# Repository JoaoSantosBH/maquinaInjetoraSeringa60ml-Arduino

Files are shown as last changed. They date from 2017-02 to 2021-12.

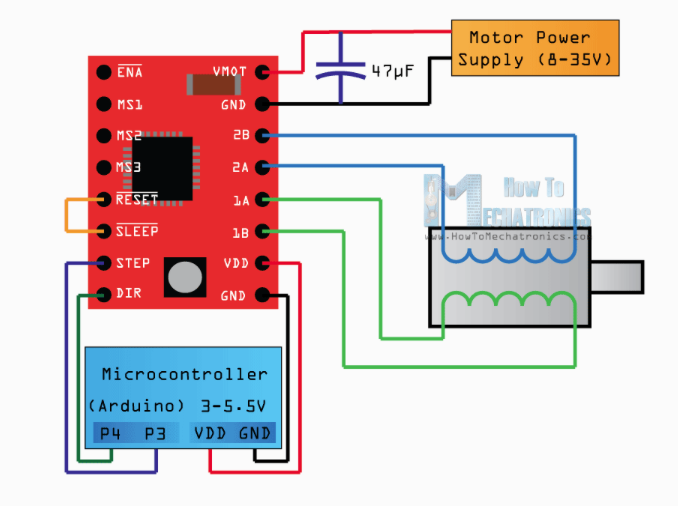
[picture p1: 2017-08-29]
docs/stepMotorA4988.png

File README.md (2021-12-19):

# Protótipo de Maquina Injetora para Seringa 60ml com Arduino


João Santos

Em 2015 devido a um estreitamento de esôfago (disfagia) causado por um câncer, minha mãe passou a se alimentar por uma sonda de [**Gastrostomia**](https://www.tuasaude.com/gastrostomia/) e a partir dai, passamos a conviver com problemas gerados pela alimentação através de sonda.

Durante dois anos observando esses problemas, me veio a motivação de construir um protótipo de uma máquina injetora para nutrição.

[Artigo](https://joaomarcelo-ms.medium.com/prot%C3%B3tipo-de-maquina-injetora-para-seringa-60ml-com-arduino-6b15f981d936)

Prototipo de maquina injetora de dieta liquida com seringa 60ML desenvolvido com Arduino;</br>

Projetada para infusão de dietas ricas em fibras e mais viscosas, em pacientes com restrição alimentar por via oral,</br>
 aumentando a qualidade alimentar do paciente, uma vez que permite alimentos mais viscosos e com isso mais ricos em fibras </br>
e nutrientes, ao contrário das dietas industrializadas que se dão por equipamentos (Equipo) que facilmente entopem,</br> impedindo o 
paciente de consumir dietas mais ricas em fibras e nutrientes;</br>

A duração da infusão é programada em 3 minutos para 60 ml de dieta, com intuito de evitar ulceração no paciente, devido ao </br>alimento 
entrar muito rapidamente, como é o caso, quando aplicado à mão, e aumentar a absorção do alimento pelo organismo.</br>

Neste caso a dieta pode ser ministrada lentamente, evitando o risco de ulcera e aumentando a absorção do alimento;</br>

Através de um App ou do botão na máquina o paciente ou seu cuidador, pode iniciar a injeção alimentar, e ao final da injeção</br>
 a maquina automaticamente retorna a posição inicial para aguardar nova carga de alimento, gerando maior conforto para o </br>paciente 
e/ou seu cuidador</br>

A máquina possui alertas visuais e sonoros para indicar seu status de funcionamento, e é portátil, podendo ser levada para onde for!</br>

Listagem dos componentes necessários:</br>
<ul>
<li>1 Arduino MEGA/UNO</li>
<li>1 buzzer</li>
<li>1 led vermelho</li>
<li>1 led verde</li>
<li>3 chaves tacteis</li>
<li>2 chaves fim de curso</li>
<li>5 resistores 100Ω</li>
<li>1 capacitor eletrolitico 100µF 16V</li>
<li>1 motor passo nema 14</li>
<li>1 drive A4988 (necessário regular a corrente para 0.7 A)</li>
<li>1 seringa 60ml</li>
<li>1 estrutura base maquina (projeto 3D para impressão em anexo)</li>
<li>1 Acoplamento Flexivel/cnc/motor Passo 5x5 Mm</li>
<li>1 barra parafuso 5mm - 1m </li>
<li>2 porcas sextavadas 5mm</li>
<li>1 protoboard</li>
<li>1 fonte 12V 1A</li>
<li>1 chapa mdf 300mm x 50mm x 6mm</li>
<li>1 rolamento 2.2cm ø</li>
<li>Kit Jumpers Macho-Macho</li>
</ul>

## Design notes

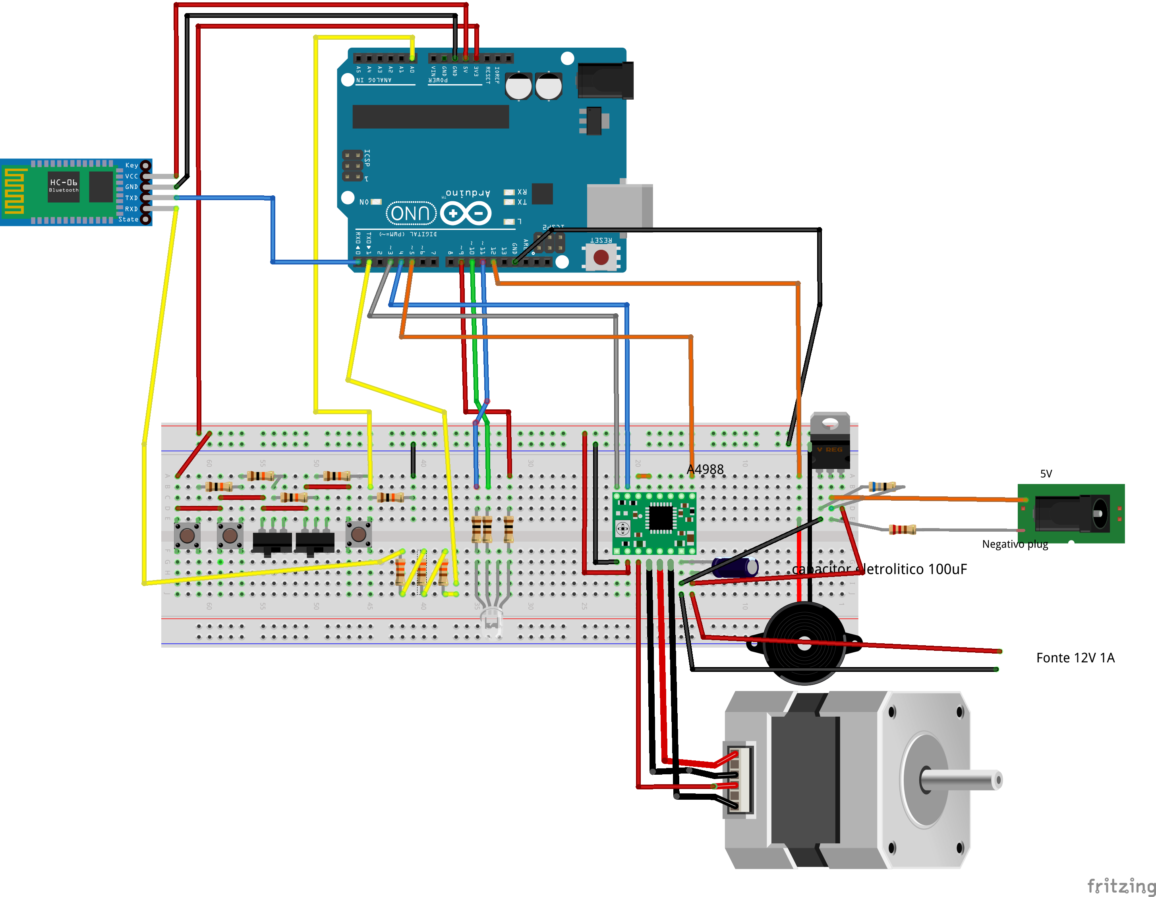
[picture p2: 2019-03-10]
docs/PROTOBOARD_uno.png

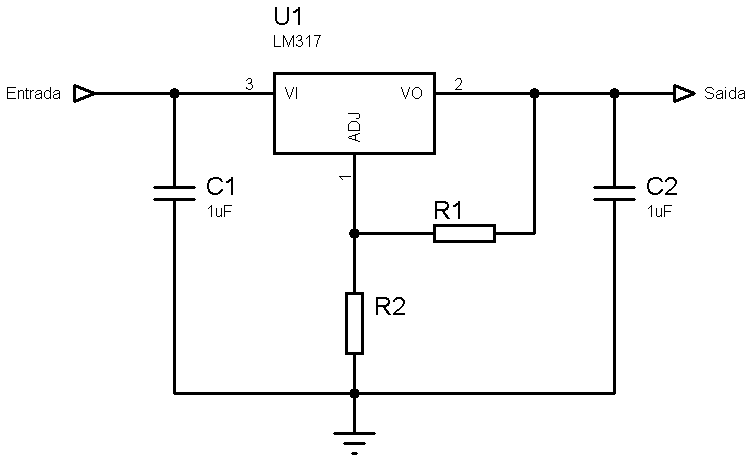
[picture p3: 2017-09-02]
docs/CILM317.png

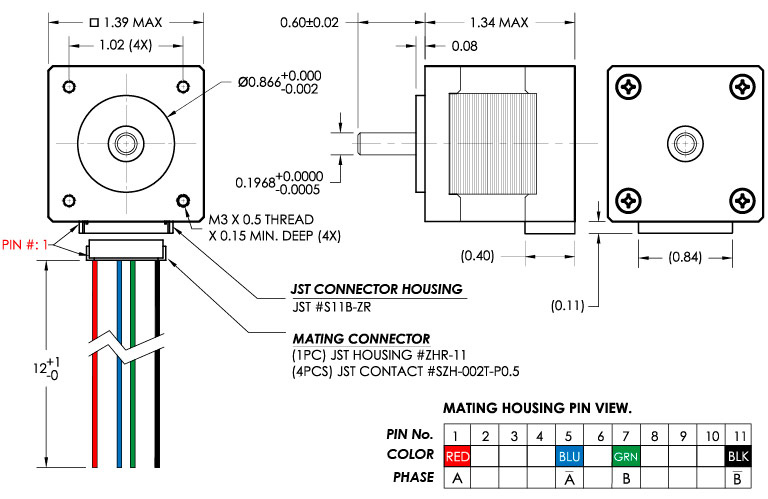
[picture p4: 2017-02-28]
docs/nema14eletric.jpg

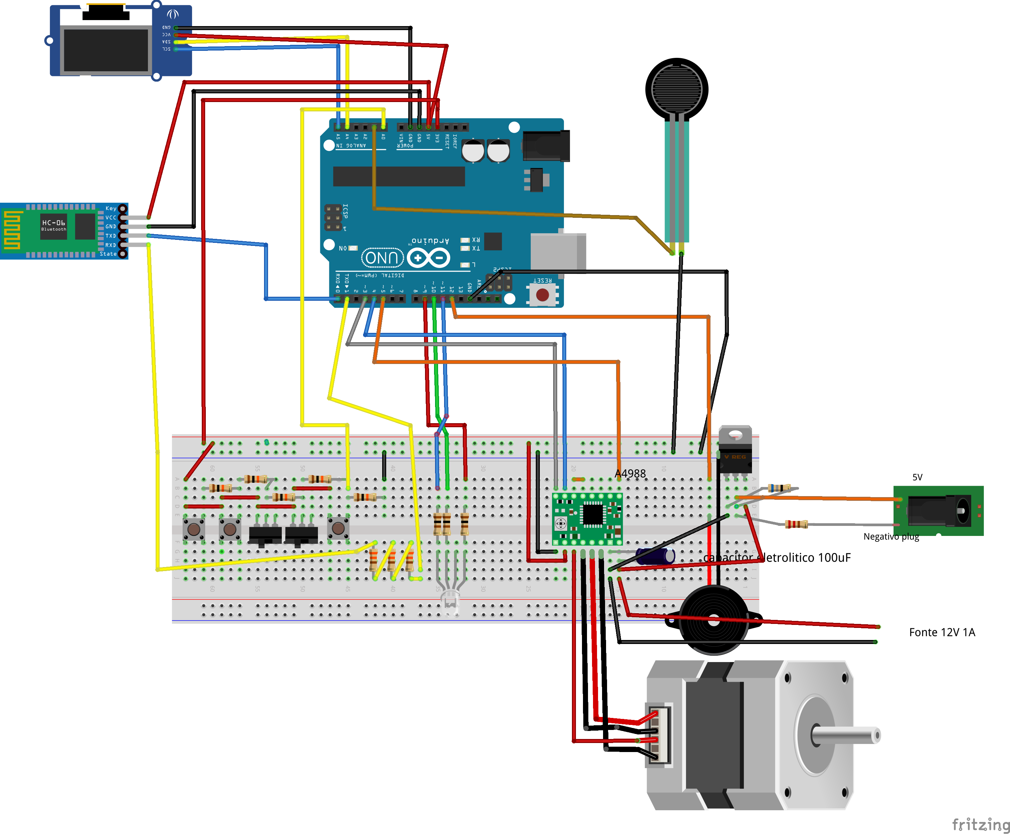
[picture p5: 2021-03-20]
fritzing/pcb_bb.png

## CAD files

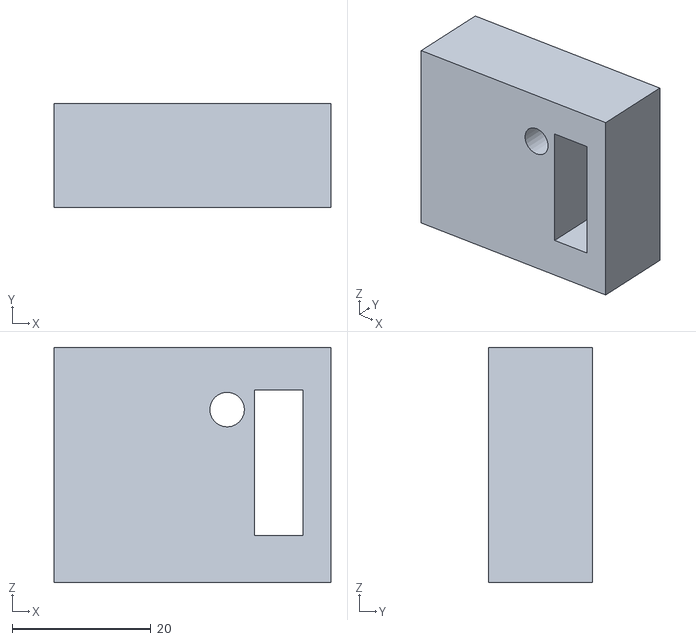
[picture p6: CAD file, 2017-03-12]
stl/FimCurso.stl
40.0 x 15.0 x 34.0

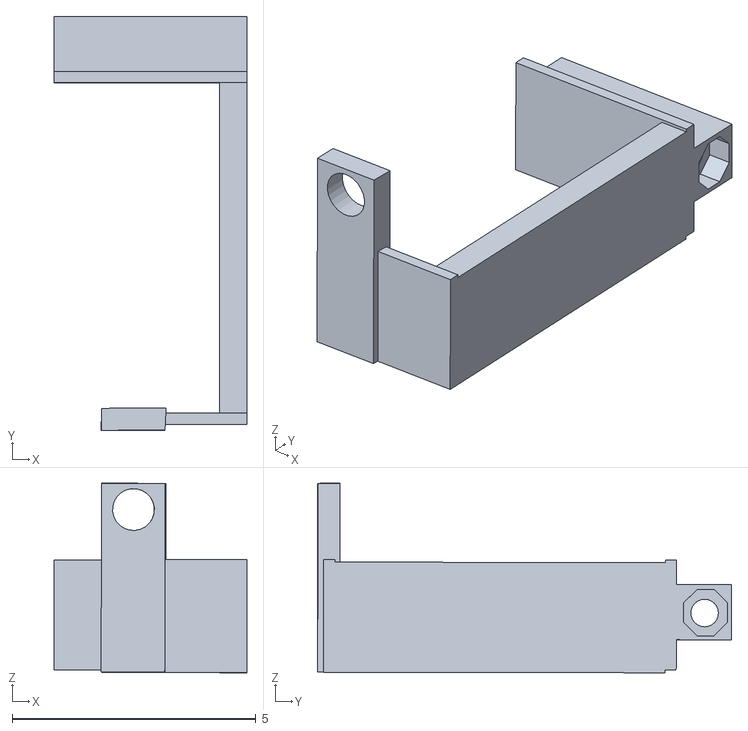
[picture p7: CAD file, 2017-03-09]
stl/suporteEmboloSeringaScale.stl
3.96 x 8.49 x 3.89

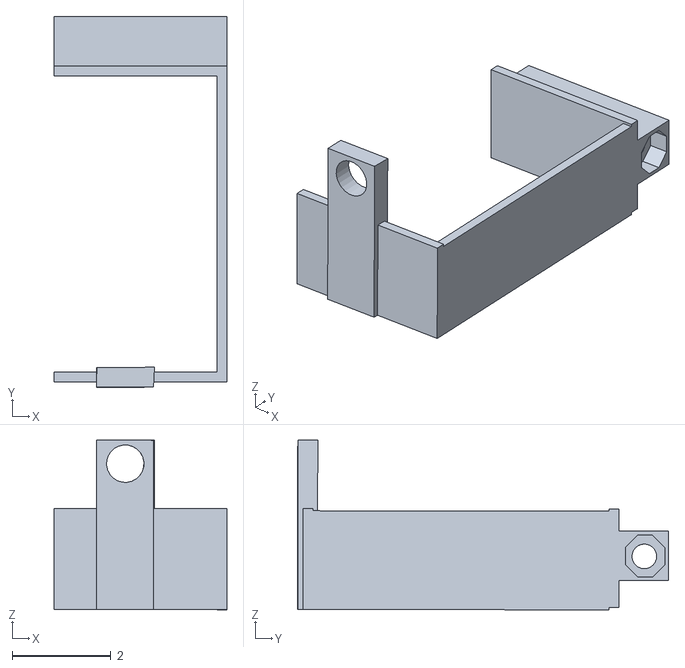
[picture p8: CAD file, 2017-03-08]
stl/SuporteEmbolo.stl
3.50 x 7.52 x 3.44

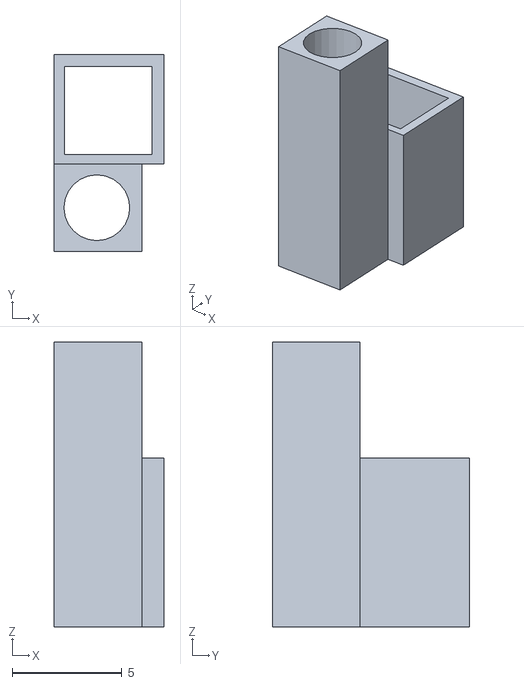
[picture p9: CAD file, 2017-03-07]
stl/estrutura.stl
5.00 x 9.00 x 13.0

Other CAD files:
old_stuff/sketchup/FimCurso.skp
old_stuff/sketchup/baeseMadeira.skp
old_stuff/sketchup/estrutura_modelo3D.skp
old_stuff/sketchup/suporteEmboloSeringa.skp
old_stuff/sketchup/suporteEmboloSeringaScale.skp
sketchup/FimCurso.skp
sketchup/baeseMadeira.skp
sketchup/estrutura_modelo3D.skp
sketchup/suporteEmboloSeringa.skp
sketchup/suporteEmboloSeringaScale.skp

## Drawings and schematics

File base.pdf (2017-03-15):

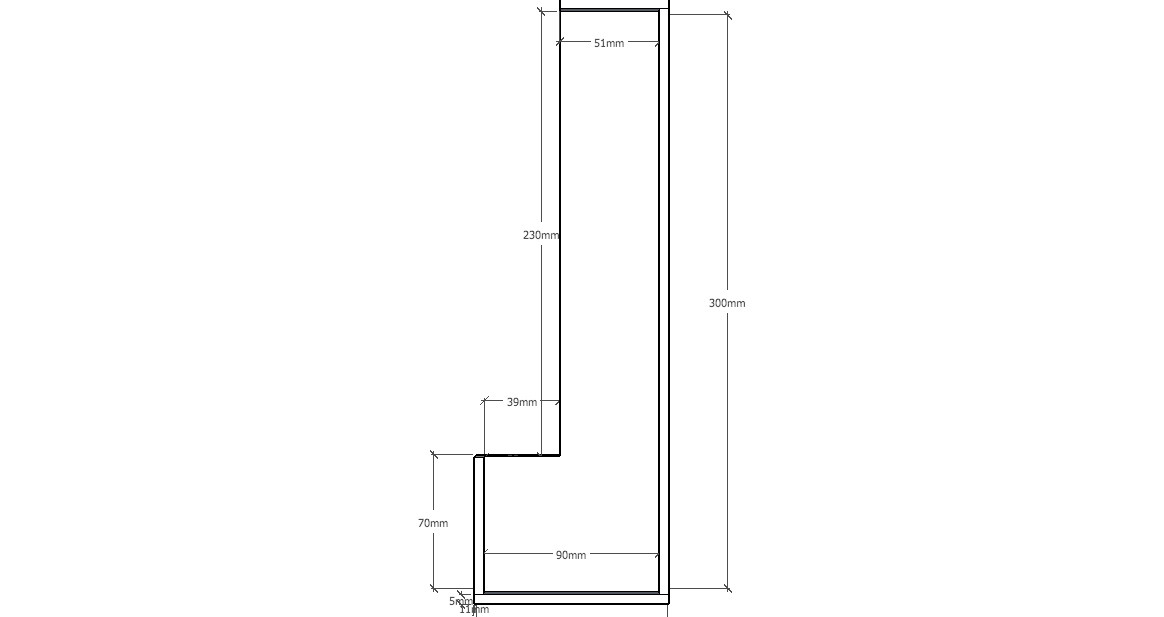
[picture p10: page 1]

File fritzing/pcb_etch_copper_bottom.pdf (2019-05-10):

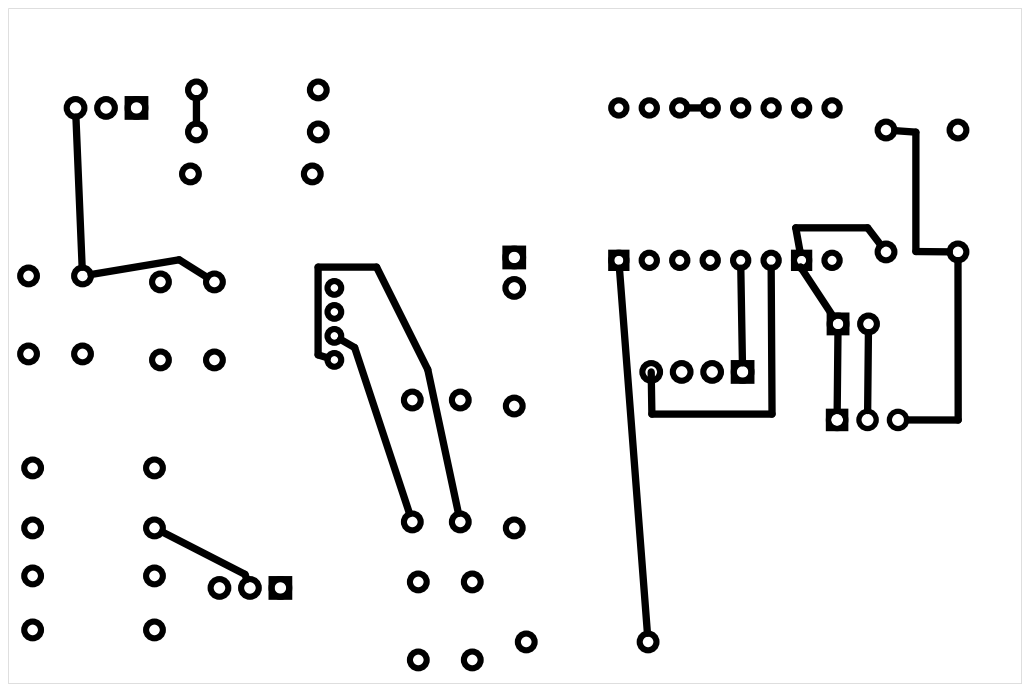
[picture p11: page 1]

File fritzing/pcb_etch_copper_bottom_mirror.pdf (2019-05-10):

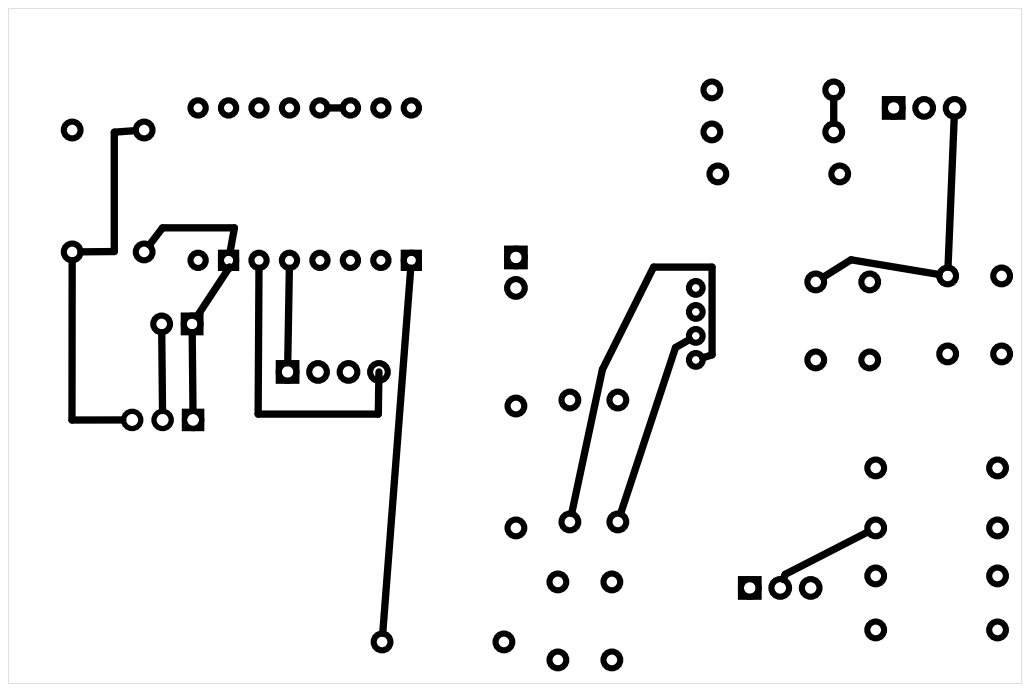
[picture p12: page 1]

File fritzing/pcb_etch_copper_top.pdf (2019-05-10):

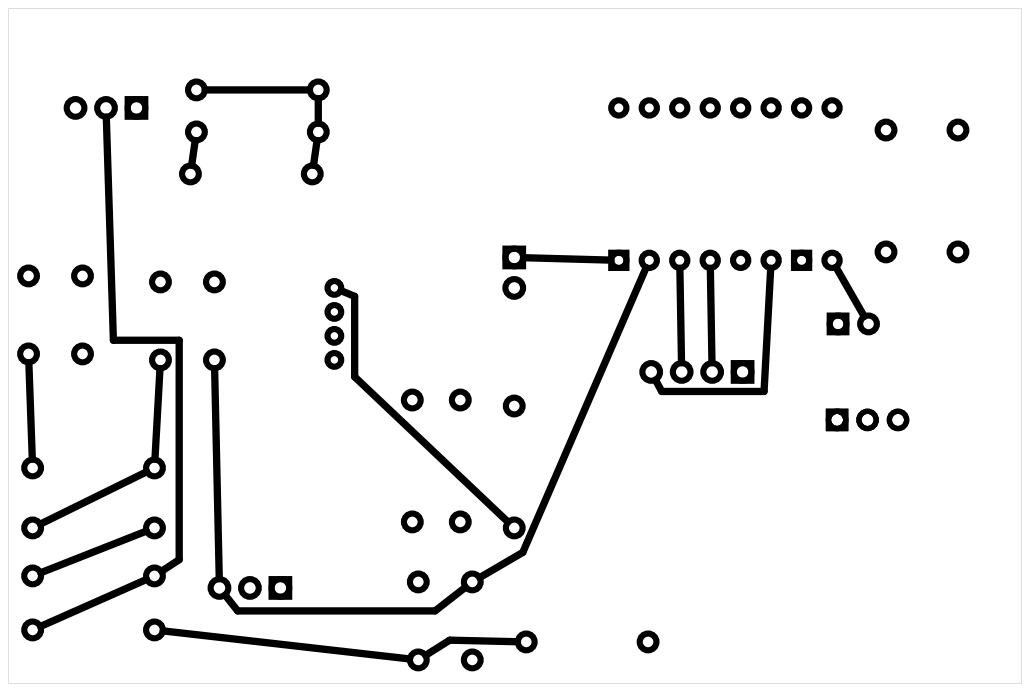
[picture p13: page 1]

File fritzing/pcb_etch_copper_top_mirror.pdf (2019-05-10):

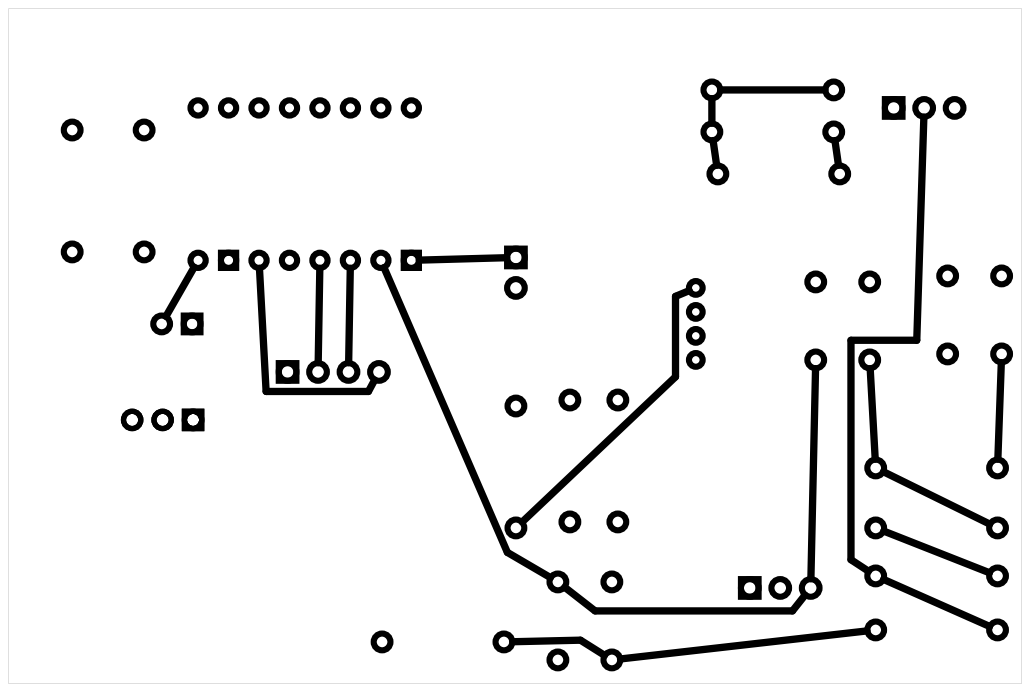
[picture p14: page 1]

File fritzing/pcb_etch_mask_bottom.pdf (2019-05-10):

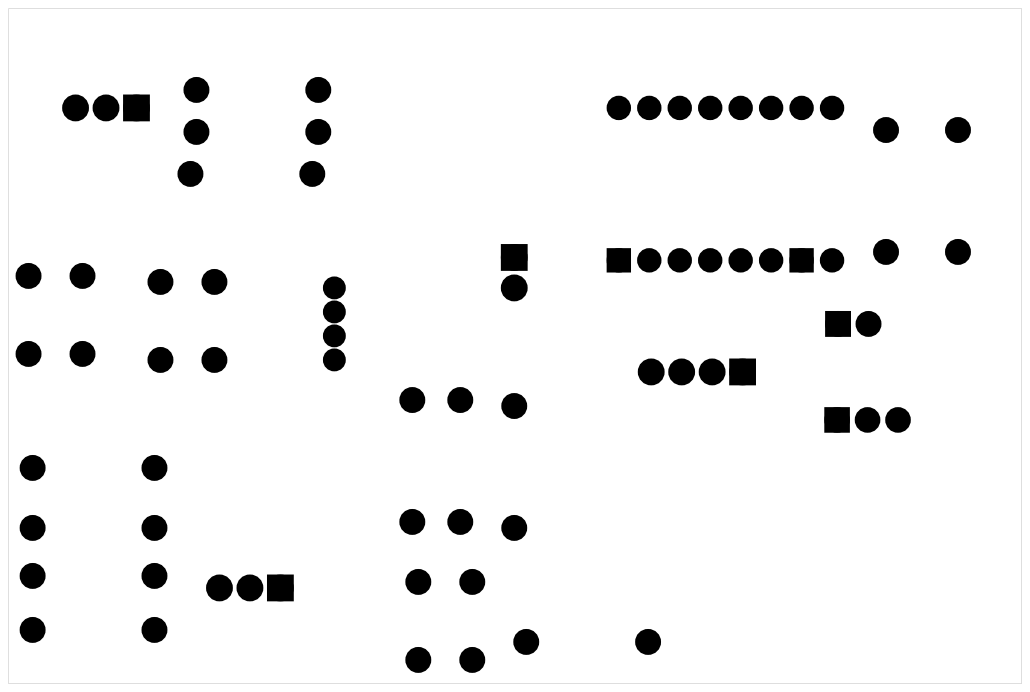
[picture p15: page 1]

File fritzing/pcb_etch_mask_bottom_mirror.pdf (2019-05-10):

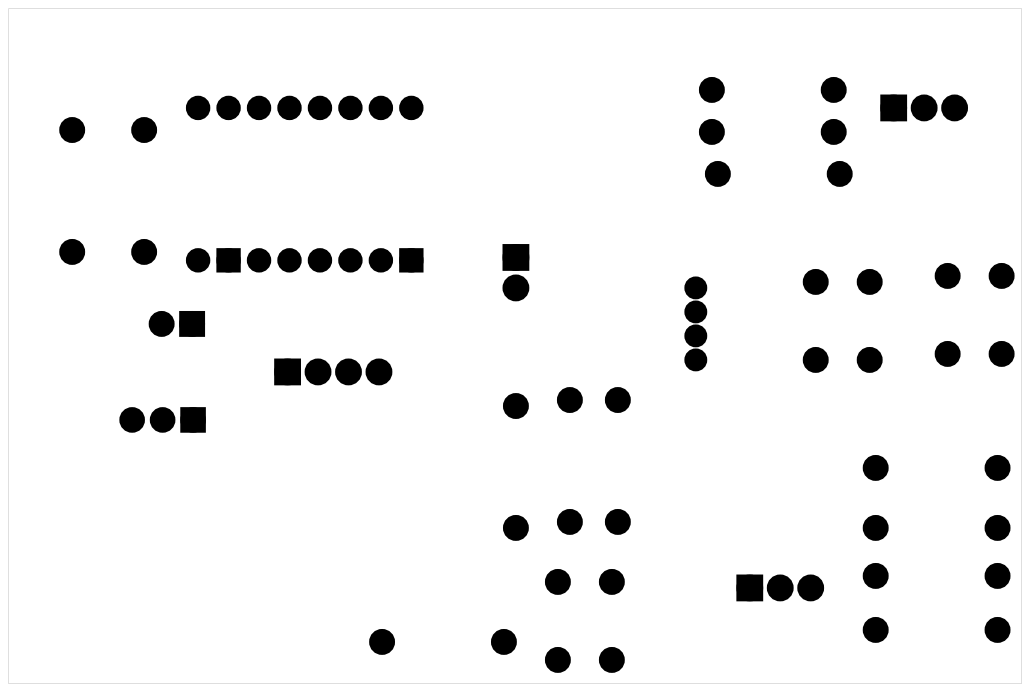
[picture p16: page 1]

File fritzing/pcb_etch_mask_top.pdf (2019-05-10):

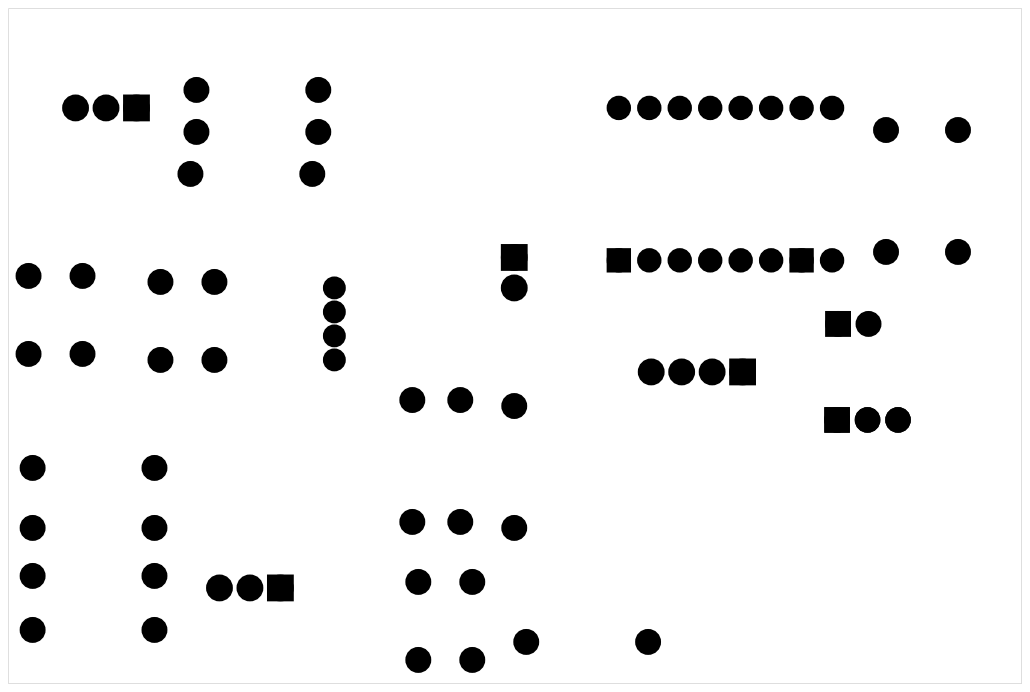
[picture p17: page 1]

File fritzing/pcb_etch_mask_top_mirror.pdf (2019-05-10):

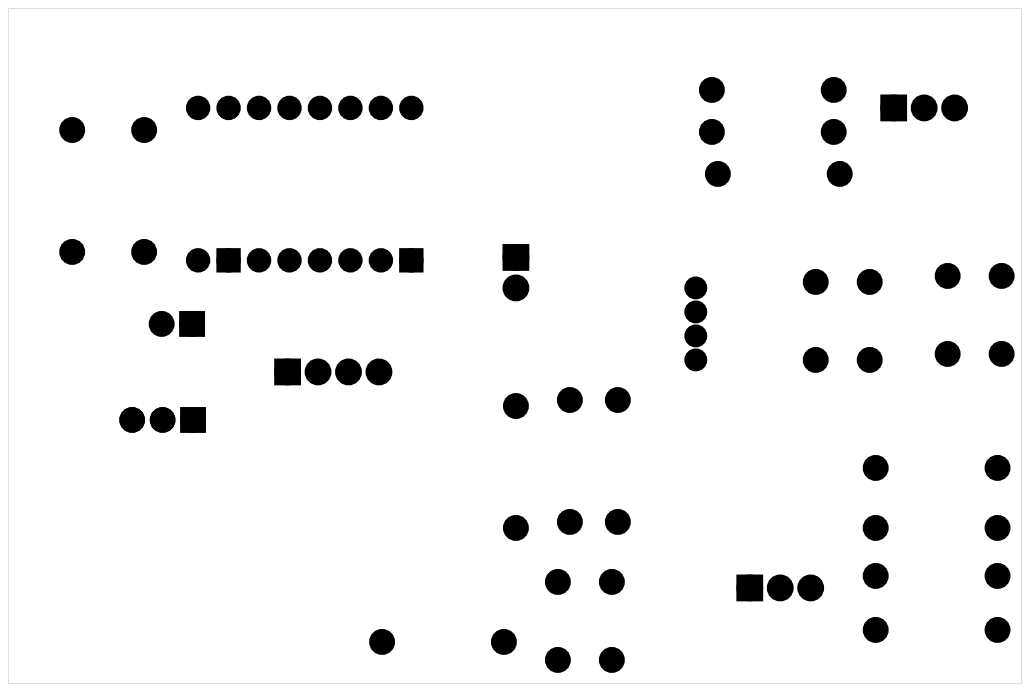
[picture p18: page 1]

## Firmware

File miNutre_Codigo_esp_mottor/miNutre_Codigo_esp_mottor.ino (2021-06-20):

//  MAQUINA INJETORA DE DIETA VIA SERINGA 60ML

// 10-03-2019
// VERSAO 1.1.0
//mar 2021

#include <AccelStepper.h>
#include <U8g2lib.h>
U8G2_SSD1306_128X64_NONAME_F_HW_I2C u8g2(U8G2_R0, /* reset=*/ U8X8_PIN_NONE, /* clock=*/ 5, /* data=*/ 4);   // ESP32 Thing, HW I2C with pin remapping

const uint8_t logo[] PROGMEM = {
  0x00, 0x00, 0x00, 0x00, 0x00, 0x00, 0x00, 0x00, 0x00, 0x00, 0x00, 0x00, 0x00, 0x00, 0x00, 0x00,
  0x00, 0x00, 0x00, 0x00, 0x00, 0x00, 0x00, 0x00, 0x00, 0x00, 0x00, 0x00, 0x00, 0x00, 0x00, 0x00,
  0x00, 0x00, 0x00, 0x00, 0x00, 0x00, 0x00, 0x00, 0x00, 0x00, 0x00, 0x00, 0x00, 0x00, 0x00, 0x00,
  0x03, 0xff, 0xff, 0xff, 0xff, 0xff, 0xff, 0xff, 0xff, 0xff, 0xff, 0xff, 0xff, 0xff, 0xff, 0xc0,
  0x07, 0xff, 0xff, 0xff, 0xff, 0xff, 0xff, 0xff, 0xff, 0xff, 0xff, 0xff, 0xff, 0xff, 0xff, 0xe0,
  0x07, 0xff, 0xff, 0xff, 0xff, 0xff, 0xff, 0xff, 0xff, 0xff, 0xff, 0xff, 0xff, 0xff, 0xff, 0xe0,
  0x07, 0x00, 0x00, 0x00, 0x00, 0x00, 0x00, 0x00, 0x00, 0x00, 0x00, 0x00, 0x00, 0x00, 0x00, 0x60,
  0x07, 0x00, 0x00, 0x00, 0x00, 0x00, 0x00, 0x00, 0x00, 0x00, 0x00, 0x00, 0x00, 0x00, 0x00, 0x60,
  0x07, 0x00, 0x00, 0x00, 0x00, 0x00, 0x00, 0x00, 0x00, 0x00, 0x00, 0x00, 0x00, 0x00, 0x00, 0x60,
  0x07, 0x00, 0x00, 0x00, 0x00, 0x00, 0x00, 0x00, 0x00, 0x00, 0x00, 0x00, 0x00, 0x00, 0x00, 0x60,
  0x07, 0x00, 0x00, 0x00, 0x00, 0x00, 0x00, 0x00, 0x00, 0x00, 0x00, 0x00, 0x00, 0x00, 0x00, 0x60,
  0x07, 0x00, 0x00, 0x00, 0x00, 0x00, 0x00, 0x00, 0x00, 0x00, 0x00, 0x00, 0x00, 0x00, 0x00, 0x60,
  0x07, 0x00, 0x00, 0x00, 0x00, 0x00, 0x01, 0xfc, 0x00, 0x00, 0x3c, 0x00, 0x00, 0x00, 0x00, 0x60,
  0x07, 0x00, 0x00, 0x00, 0x00, 0x00, 0x1f, 0xfc, 0x00, 0x01, 0xfe, 0x00, 0x00, 0x00, 0x00, 0x60,
  0x07, 0x00, 0x00, 0x00, 0x00, 0x01, 0xff, 0xff, 0xc0, 0x1f, 0xfc, 0x00, 0x00, 0x00, 0x00, 0x60,
  0x07, 0x00, 0x00, 0x00, 0x00, 0x0f, 0xff, 0xff, 0xe0, 0xff, 0xf8, 0x00, 0x00, 0x00, 0x00, 0x60,
  0x07, 0x00, 0x00, 0x00, 0x00, 0xff, 0xff, 0xff, 0xef, 0xff, 0xc0, 0x00, 0x00, 0x00, 0x00, 0x60,
  0x07, 0x00, 0x00, 0xe0, 0x07, 0xff, 0xff, 0xff, 0xff, 0xfc, 0x00, 0x00, 0x00, 0x00, 0x00, 0x60,
  0x07, 0x00, 0x01, 0xf0, 0x3f, 0xff, 0xff, 0xff, 0xff, 0xe0, 0x00, 0x00, 0x1f, 0x00, 0x00, 0x60,
  0x07, 0x00, 0x01, 0xf3, 0xff, 0xff, 0xff, 0xff, 0xfe, 0x00, 0x00, 0x00, 0x60, 0x80, 0x00, 0x60,
  0x07, 0x00, 0x01, 0xff, 0xff, 0xff, 0xff, 0xff, 0xf0, 0x00, 0x00, 0x00, 0xc0, 0x40, 0x00, 0x60,
  0x07, 0x00, 0x01, 0xff, 0xff, 0xff, 0xff, 0xff, 0xf0, 0x00, 0x00, 0x00, 0x9e, 0x20, 0x00, 0x60,
  0x07, 0x00, 0x00, 0xff, 0xff, 0xff, 0xff, 0xff, 0xf0, 0x00, 0x00, 0x01, 0x11, 0x10, 0x00, 0x60,
  0x07, 0x00, 0x00, 0xff, 0xff, 0xff, 0xff, 0xff, 0xf0, 0x00, 0x00, 0x01, 0x11, 0x10, 0x00, 0x60,
  0x07, 0x08, 0x00, 0xff, 0xff, 0xff, 0xff, 0xff, 0xc0, 0x00, 0x00, 0x01, 0x1e, 0x10, 0x00, 0x60,
  0x07, 0x1e, 0x03, 0xff, 0xff, 0xff, 0xff, 0xff, 0xc0, 0x00, 0x00, 0x01, 0x12, 0x10, 0x00, 0x60,
  0x07, 0x3e, 0x3f, 0xff, 0xff, 0xff, 0xff, 0xff, 0xc0, 0x00, 0x00, 0x01, 0x13, 0x10, 0x00, 0x60,
  0x07, 0x3f, 0xff, 0xff, 0xff, 0xff, 0xff, 0xff, 0x80, 0x00, 0x00, 0x00, 0x91, 0x20, 0x00, 0x60,
  0x07, 0x3f, 0xff, 0xff, 0xff, 0xff, 0xff, 0xff, 0x00, 0x00, 0x00, 0x00, 0xc0, 0x60, 0x00, 0x60,
  0x07, 0x1f, 0xff, 0xff, 0xff, 0xff, 0xff, 0xfc, 0x00, 0x00, 0x00, 0x00, 0x60, 0x80, 0x00, 0x60,
  0x07, 0x1f, 0xff, 0xff, 0xff, 0xff, 0xff, 0xc0, 0x00, 0x00, 0x00, 0x00, 0x1f, 0x00, 0x00, 0x60,
  0x07, 0x1f, 0xff, 0xff, 0xff, 0xff, 0xfe, 0x00, 0x00, 0xc0, 0x00, 0x00, 0x00, 0x00, 0x00, 0x60,
  0x07, 0x1f, 0xff, 0xff, 0xff, 0xff, 0xe0, 0x00, 0x03, 0xc0, 0x00, 0x00, 0x00, 0x00, 0x00, 0x60,
  0x07, 0x1f, 0xff, 0xff, 0xff, 0xff, 0x00, 0x00, 0x0f, 0xc0, 0x00, 0x00, 0x00, 0x00, 0x00, 0x60,
  0x07, 0x0f, 0xff, 0xff, 0xff, 0xf0, 0x00, 0x00, 0x3f, 0xc0, 0x00, 0x00, 0x00, 0x00, 0x00, 0x60,
  0x07, 0x0f, 0xff, 0xdf, 0xff, 0x00, 0x00, 0x00, 0x7f, 0xc0, 0x00, 0x00, 0x00, 0x00, 0x00, 0x60,
  0x07, 0x0f, 0xfe, 0x1f, 0xf0, 0x00, 0x00, 0x00, 0x7f, 0xc0, 0x00, 0x00, 0x00, 0x00, 0x00, 0x60,
  0x07, 0x07, 0xe0, 0x0f, 0xc0, 0x00, 0x00, 0x00, 0xff, 0xc0, 0x00, 0x00, 0x00, 0x00, 0x00, 0x60,
  0x07, 0x07, 0xe0, 0x0f, 0xc0, 0x00, 0x00, 0x00, 0xff, 0xc0, 0x00, 0x00, 0x00, 0x00, 0x00, 0x60,
  0x07, 0x07, 0xe0, 0x0f, 0xc0, 0x00, 0x00, 0x00, 0xff, 0xc0, 0x00, 0x00, 0x00, 0x00, 0x00, 0x60,
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
};

#define STEP_PIN                   0
#define DIRECTION_PIN              2
#define MOTOR_ENABLE_PIN          15
#define PRESSURE_SENSOR           A0
#define BUTTONS                   A0
#define BUZZER                     16
#define BLUE                      13
#define GREEN                     12
#define RED                       14


AccelStepper myStepMotor(AccelStepper::DRIVER, STEP_PIN, DIRECTION_PIN );

char command;
String stringBluetooth;

String MACHINE_NAME = "m i N U T R E";
String RECALL = "RECALLn";
String WAIT   = "WAITING";
String INJECT = "INJECTn";
String START = "STARTIn";
String LOGO = "miNUTRE";

long myStepRevolutions = -1000000;

int preto     [3]  = { 0, 0, 0 };
int dimbranco [3]  = { 30, 30, 30};
int redValue = preto[0];
int greenValue = preto[1];
int blueValue = preto[2];
// VARIAVEIS DE CORES
int nRed = redValue;
int nGreen = greenValue;
int nBlue = blueValue;

int buttonBusStatus = 0;
int isInjecting  = 0;
int isWaiting = 1;
int isRecalling = 0;
int  botI = 1;
int  botR = 0;
int  botP = 0;
int  fcI  = 0;
int  fcR  = 0;
int pressureReading;
int incomingByte = 0;
int PULSE_WIDTH = 3;

int BT01_MIN = 200;
int BT01_MAX = 228;
int BT02_MIN = 240;
int BT02_MAX = 297;
int FDC01_MIN = 500;
int FDC01_MAX = 550;
int FDC02_MIN = 1000;
int FDC02_MAX = 1030;

void setup() {
  Serial.begin(115200);
  setupInOut();
  putMachineInReadyState();
  setupOled();
  printStatusOnSerial();
  drawInit();
  turnOnGreenLight();
  drawLogo();

}

void loop() {

  bluetoothCommandsListener();
  readComponentStatus();
  checkPressedButtons();
  checkBluetoothCommands();
  readInjectionPressure() ;
  //M O C K

  if (Serial.available() > 0) {
    // read the incoming byte:
    incomingByte = Serial.read();

    // say what you got:
    Serial.print("I received: ");
    Serial.println(incomingByte);

    if (incomingByte == 49) {
      startInjection() ;
    } else  if (incomingByte == 50) {
      stopInjectionAndPickup() ;
    } else  if (incomingByte == 48) {
      stopMachine() ;
    }
  }
  //M O C K
  myStepMotor.run();
}


void startInjection() {
  Serial.println("startInjection");
  settingInjectionStatus();
  turnOnBlueLight();
  drawInjet();
  settingInjectionMotor();
  stringBluetooth = "";
  printStatusOnSerial();
}

void stopInjectionAndPickup() {
  Serial.println("stopInjectionAndPickup");
  turnOnVioletLight();
  drawWait();
  settingStopRecallStatus();
  settingWaitMotor();
  printStatusOnSerial();
  pickupRecall();
}

void pickupRecall() {
  Serial.println("pickupRecall");
  settingRecallStatus();
  turnOnWhiteLight();
  drawRecall();
  settingRecallMotor();
  printStatusOnSerial();
}

void stopMachine() {
  Serial.println(" stopMachine");
  turnOnRedLight();
  drawWait();
  settingWaitStatus();
  settingWaitMotor();
  printStatusOnSerial();
  playHappyMelody();
}

void pressurePanic() {
  Serial.println(" pressurePanic");
  Serial.println("a pressão atingiu niveis alarmantes");
  turnOnRedLight();
  drawLogo();
  settingWaitStatus();
  settingWaitMotor();
  playImperialMarch();
  printStatusOnSerial();
}

void backALitle() {
  Serial.println("backALitle");
  turnOnGreenLight();
  drawLogo();
  settingWaitStatus();
  settingBackLittleMotor();
  delay(1000);
  drawWait();
  printStatusOnSerial();

}

void colorCrossFade(int cor[3]) {
  int R = (cor[0] * 255) / 100;
  int G = (cor[1] * 255) / 100;
  int B = (cor[2] * 255) / 100;
  int sweepRed = calcColorSweep(nRed, R);
  int sweepGreen = calcColorSweep(nGreen, G);
  int sweepBlue = calcColorSweep(nBlue, B);

  for (int i = 0; i <= 1020; i++) {
    redValue = calculateValue(sweepRed, redValue, i);
    greenValue = calculateValue(sweepGreen, greenValue, i);
    blueValue = calculateValue(sweepBlue, blueValue, i);
    analogWrite(RED, redValue);   // Write current valorues to LED pins
    analogWrite(GREEN, greenValue);
    analogWrite(BLUE, blueValue);
    delay(10);
  }
  nRed = redValue;
  nGreen = greenValue;
  nBlue = blueValue;
  delay(0);
}

int calcColorSweep(int previousValue, int finalValue) {
  int sweep = finalValue - previousValue;
  if (sweep) {
    sweep = 1020 / sweep;
  }
  return sweep;
}

int calculateValue(int sweep, int valor, int i) {
  if ((sweep) && i % sweep == 0) {
    if (sweep > 0) {
      valor += 1;
    }
    else if (sweep < 0) {
      valor -= 1;
    }
  }

  if (valor > 255) {
    valor = 255;
  }
  else if (valor < 0) {
    valor = 0;
  }
  return valor;
}

void turnOnGreenLight() {
  digitalWrite(GREEN, 255);
  digitalWrite(RED, 0);
  digitalWrite(BLUE, 0);
}
void turnOnRedLight() {
  digitalWrite(GREEN, 0);
  digitalWrite(RED, 255);
  digitalWrite(BLUE, 0);
}
void turnOnBlueLight() {
  digitalWrite(GREEN, 0);
  digitalWrite(RED, 0);
  digitalWrite(BLUE, 255);
}

void turnOnVioletLight() {
  digitalWrite(GREEN, 0);
  digitalWrite(RED, 255);
  digitalWrite(BLUE, 255);
}

void turnOnWhiteLight() {
  digitalWrite(GREEN, 255);
  digitalWrite(RED, 255);
  digitalWrite(BLUE, 255);
}

// THE IMPERIAL MARCH - John Williams
void playImperialMarch() {
  tone(BUZZER, 1500);
  delay(500);
  noTone(BUZZER);
  delay(50);
  tone(BUZZER, 1500);
  delay(500);
  noTone(BUZZER);
  delay(50);
  tone(BUZZER, 1500);
  delay(500);
  noTone(BUZZER);
  delay(50);
  tone(BUZZER, 1200);
  delay(250);
  tone(BUZZER, 1850);
  delay(250);
  noTone(BUZZER);
  delay(50);
  tone(BUZZER, 1500);
  delay(500);
  noTone(BUZZER);
  delay(50);
  tone(BUZZER, 1200);
  delay(250);
  tone(BUZZER, 1850);
  delay(250);
  tone(BUZZER, 1500);
  delay(500);
  noTone(BUZZER);
  delay(500);
  ///////////////////
  tone(BUZZER, 2220);
  delay(500);
  noTone(BUZZER);
  delay(50);
  tone(BUZZER, 2220);
  delay(500);
  noTone(BUZZER);
  delay(50);
  tone(BUZZER, 2220);
  delay(500);
  tone(BUZZER, 2369);
  delay(250);
  tone(BUZZER, 1850);
  delay(250);
  noTone(BUZZER);
  delay(50);
  tone(BUZZER, 1500);
  delay(500);
  noTone(BUZZER);
  delay(50);
  tone(BUZZER, 1200);
  delay(250);
  tone(BUZZER, 1850);
  delay(250);
  tone(BUZZER, 1500);
  delay(500);
  noTone(BUZZER);
}

void playHappyMelody() {
  tone(BUZZER, 1046);
  delay(125);
  noTone(BUZZER);
  delay(50);
  tone(BUZZER, 1318);
  delay(125);
  noTone(BUZZER);
  delay(50);
  tone(BUZZER, 1567);
  delay(125);
  noTone(BUZZER);
  delay(50);
  tone(BUZZER, 2093);
  delay(125);
  noTone(BUZZER);
  delay(50);
  tone(BUZZER, 2637);
  delay(125);
  noTone(BUZZER);
  delay(50);
  tone(BUZZER, 1046);
  delay(125);
  noTone(BUZZER);
  delay(50);
  tone(BUZZER, 1567);
  delay(125);
  noTone(BUZZER);
  delay(50);
  tone(BUZZER, 2637);
  delay(125);
  noTone(BUZZER);
  delay(50);
  tone(BUZZER, 2093);
  delay(250);
  noTone(BUZZER);
  delay(50);
}

void drawInit() {
  u8g2.firstPage();
  do {
    u8g2.setFont(u8g2_font_ncenB14_tr);
    u8g2.drawStr( 5, 15, "(31)988470290");
    u8g2.setFont(u8g2_font_helvR14_tr);
    u8g2.drawStr( 10, 57, START.c_str());
    //frame
    u8g2.drawRFrame(0, 18, 128, 46, 4);
  } while ( u8g2.nextPage() );
}

void drawInjet() {
    u8g2.firstPage();
    do {
      u8g2.setFont(u8g2_font_helvR14_tr);
      u8g2.drawStr( 5, 15, MACHINE_NAME.c_str());
      u8g2.setFont(u8g2_font_helvR14_tr);
      u8g2.drawStr( 10, 57, INJECT.c_str());
      //frame
      u8g2.drawRFrame(0, 18, 128, 46, 4);
    } while ( u8g2.nextPage() );
}

void drawRecall() {
    u8g2.firstPage();
    do {
      u8g2.setFont(u8g2_font_helvR14_tr);
      u8g2.drawStr( 5, 15, MACHINE_NAME.c_str());
      u8g2.setFont(u8g2_font_helvR14_tr);
      u8g2.drawStr( 10, 57, RECALL.c_str());
      //frame
      u8g2.drawRFrame(0, 18, 128, 46, 4);
    } while ( u8g2.nextPage() );
}
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

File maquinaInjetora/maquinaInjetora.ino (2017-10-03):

//  MAQUINA INJETORA DE DIETA VIA SERINGA 60ML


// A IMPLEMENTAR 
// 01- detectar torque do motor de giro para possivel entupimento do sistema E PAUSAR A MAQUINA
//usando sensor de peso no mecanismo que empuraa o embolo, 
// 02- colocar Led unico RGB, 
// 03- Display LCD, 
// 04 -mudar musica, colocar uma melodia para cada estado
// 05- refatorar codigo em função das portas analógicas, 
// 06- redefinir estrutura
// 07- imlpementar luz led inicialização sweep cores


// VERSAO 1.0.0

//IMPORTANDO BIBLIOTECA MOTOR PASSO
#include <AccelStepper.h>

//DECLARANDO OS COMPONENTES DA MAQUINA INJETORA
int ledVerde                     = 13;
int buzzer                       = 12;
int botInjetar                   = 11;
int botRecolher                  = 10;
int fimCursoInjecaoCompleto      =  9;
int fimCursoRecolhimentoCompleto =  8;
int ledVermelho                  =  7;
int botParar                     =  6;

// Definicao pino ENABLE MOTOR PASSO
int pino_enable = 5;

// PINOS STEP e DIR MOTOR PASSO
AccelStepper motorPasso(1,4,3 );

//DEFINE QUANTIDADE GIROS DO MOTOR, 
//COMO HÁ UM FIM DE CURSO IMPLEMENTOU_SE UM NUMERO MUITO GRANDE DE VOLTAS
long passo = 1000000;

//VARIAVEIS QUE VAO DETECTAR O ESTADO DE CADA BOTAO
int estadoBotaoInje =        0;
int estadoBotaoRecolhe =     0;
int estadoBotaoParar =       0;

//VARIAVEIS QUE VAO DETECTAR O ESTADO DE CADA FIM DE CURSO
int estadoFimInjCompleto =   0;
int estadoFimRecolhimento =  0;

//VARIAVEIS QUE DETECTAM ESTADOS DE FUNCIONAMENTO
int estaInjetando  = 0;
int estaAguardando = 1;
int estaRecolhendo = 0;

//DETECTA TEMPO EM QUE BOTAO FOI PRESSIONADO
unsigned long changeTime; 

//SETUP DOS COMPONENTES
void setup() {

pinMode(botInjetar,INPUT);
pinMode(botRecolher,INPUT);
pinMode(botParar, INPUT);
pinMode(fimCursoInjecaoCompleto, INPUT);
pinMode(fimCursoRecolhimentoCompleto,INPUT);                     
pinMode(ledVerde,OUTPUT);
pinMode(ledVermelho, OUTPUT);
pinMode(buzzer,OUTPUT);
pinMode(pino_enable, OUTPUT);

// CONFIGURTACOES INICIAIS MOTOR PASSO - INICIAR PARADO
motorPasso.move(0);
digitalWrite(pino_enable, HIGH);

apagarLedVermelho();
acenderLedVerde();

//INICIA COMUNICACAO SERIAL
Serial.begin(9600);
Serial.print("Maquina inicializada");
}


void loop() {
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

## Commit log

2017-02-28 PRIMEIRA VERSAO
    [maquinaInjetora.fzz, maquina_SKETCHUP.skp, maquina_arquivo_impressao3D.stl]
2017-03-01 revisão
    [maquinaInjetora.fzz]
2017-03-01 nova versão
    [maquina_arquivo_impressao3D.stl]
2017-03-02 renomeados
    renomeados arquivos para melhor entendimento
    [arquivo_impressao3D.stl, estrutura_modelo3D.skp, pcb.fzz]
2017-03-07 alteracoes
    Alterei tamanho do suporte de rolimã
    [suporteEmbolo.skp, suporteEmbolo.stl]
2017-03-07 correcao
    Existe uma angulação que deve ser corrigida no lugar do eixo e das
    porcas
    [suporteEmbolo.skp, suporteEmbolo.stl]
2017-03-08 correção
    correção definitiva de alinhamento dos eixos X,Y, Z da partes que
    estavam fora de eixo
    [suporteEmbolo.skp, suporteEmbolo.stl]
2017-03-08 Correção eixos
    Correção de eixos X,Y,Z dos objetos
    [SuporteEmbolo.stl]
2017-03-08 arquivo redundante
    [suporteEmbolo~.skp]
2017-03-08 arquivo correto
    Correções eixos 3D
    [suporteEmboloSeringa.skp]
2017-03-08 correção
    corrigindo nested events no 3D
    [FimCurso.skp, FimCurso~.skp, suporteEmboloSeringa.skp, suporteEmboloSeringa~.skp]
2017-03-08 sol gerado
    após corrigir nestes events
    [FimCurso.stl]
2017-03-09 Redesenho
    Correção da espessura da peça para reforçar, e aumento da escala para
    tubo ficar com 6mm de diâmetro não gerando atrito com o parafuso de 5mm
    além de acomodar as porcas de 5mm com delicadeza
    [suporteEmboloSeringaScale.skp, suporteEmboloSeringaScale.stl]
2017-03-15 correção
    [baeseMadeira.skp]
2017-03-20 tentativa correcta
    recolhimento agora funciona conforme esperado, o botão parar para, mas
    não executa o que está no escopo de seu método, não faz nada, o que
    leva a crer que algo está errado com ele
2017-03-25 Correção
    Correção do retorno de embolo
2017-08-16 16ago2017
    corrigindo e depurando código depois de alguns meses parado
2017-08-29 20170829
    Anotações e arquivos referentes ao motor de passo e sua secagem
    [pcb.fzz]
2017-08-30 edição de pendencias
2017-09-02 CI5v
    Inclusão do CILM317 para reduzir de 12V p 5 V
    [pcb.fzz]
2017-09-15 Revisao
    Troca do Mega pelo Uno, revisão na PCB, revisão nas conexões
    [pcb.fzz]
2017-09-16 alteração dos arquivos
    [FimCurso.skp, FimCurso.stl, SuporteEmbolo.stl, baeseMadeira.skp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]
2017-09-19 Face Simplesmples
    Redução da PCB de dupla face para face si
2017-09-21 Correção PCB
    Desenho com uma camada de cobre, sem conflitos de trilhas
2017-09-30 Upando todos arquivos
    [FimCurso.skp, FimCurso.stl, SuporteEmbolo.stl, Workbook1.xlsx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]
2017-10-07 NovaProtBoard
    Desenho da nova protoboard com o barramento de botões e fim de curso
    utilizando a porta A0 do arduino
    [pcb.fzz]
2017-10-07 NovoCodigo
    Novo código pro barramento de botões + fdc e também para o LedRGB,
    agora a maquina não tem mais o botão recolher e seu recolhimento foi
    automatizado
2017-10-19 inserção do botão pressao
    Inserção do botão de pressão no barramento analógico
    [pcb.fzz]
2019-05-10 rename dir
    [pcb.fzz]
2021-03-19 melhorando codigo
    [pcb.fzz]
2021-06-13 adicionando ESP - Motor
2021-06-14 Oled + Buzzer + Led RGB
